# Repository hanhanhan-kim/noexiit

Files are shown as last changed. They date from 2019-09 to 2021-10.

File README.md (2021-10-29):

# NOEXIIT
> "*Hell is other [insects].*"
>
> \- Insects

NOEXIIT, or *NOvel Ethological X-Insect Interaction Task*, is a behaviour rig for presenting an ethological stimulus to an insect tethered on a floating ball. We originally developed NOEXIIT to present different kinds of pinned insects to a tethered walking beetle. 

This repository houses the software for controlling NOEXIIT. It is  a `pip`-installable Python package by the same name and is a CLI. It includes commands for calibrating and testing the rig, as well as commands for acquiring experimental data. I have tested the NOEXIIT CLI on Ubuntu 18.04. 

In addition to the CLI software, the repository features a `hardware/` directory, which contains all necessary custom design files, datasheets, a bill of materials, and assembly tips. 

## Installation:

1. Clone this repository:

   ```bash
   git clone https://github.com/hanhanhan-kim/noexiit
   ```

2. Install the Anaconda environment from the repo's root directory, where `conda_env.yaml` is housed:

   ```bash
   conda env create -f conda_env.yaml
   ```

   It will create an environment called `noexiit`.

3. Activate the environment:

   ```bash
   conda activate noexiit
   ```

4. Install the `noexiit` Python package from the repo's `software/` subdirectory:

   ```bash
   pip install -e .
   ```

## Dependencies:

In addition to the `noexiit` Python package installation, additional non-Python software and firmware must be installed. They are as follows:

### Spinnaker 

I use FLIR Blackfly S cameras (BFS-U3-04S2M-CS) and Spinnaker 1.27.0.48 for Ubuntu 18.04. This Spinnaker version is no longer available on the FLIR website and requires e-mailing FLIR customer support.  

### FicTrac

[My fork](https://github.com/hanhanhan-kim/fictrac_noexiit) of [Richard Moore's official `fictrac` repo](https://github.com/rjdmoore/fictrac) requires low-level software dependencies:

- `vcpkg` rolled back to commit `85211f3ab66e15c7669a1c14a25564afcf31e2e6`. 
- [cmake v.3.15.0](https://github.com/Kitware/CMake/releases/tag/v3.15.0).

### LabJack U3 DAQ

I use the LabJack U3-HV as my DAQ, which synchronizes my data streams in hardware.  Instructions for installing the `exodriver` library necessary for using the LabJack U3-HV are available [here](https://labjack.com/support/software/installers/exodriver).  I use LabJack's [Python module](https://github.com/labjack/LabJackPython) to interface with the LabJack U3-HV. Set up of the Anaconda environment already installs the LabJack Python module.

### Firmware

#### Multi-camera external trigger

[My fork](https://github.com/hanhanhan-kim/autostep) of [Will Dickson's official `camera_trigger` repo](https://github.com/willdickson/camera_trigger) requires firmware dependencies on an ATmega328P MCU. I use the following Arduino IDE dependencies:

- TimerOne v1.1.0
- Streaming v5.0.0
- ArduinoJson v5.13.5 (is _not_ compatible with v6.0.0+)
- Array v1.1.2 

Set up of the Anaconda environment already installs the software dependencies for [`camera_trigger`](https://github.com/hanhanhan-kim/autostep).

#### Stepper and servo motors

[My fork](https://github.com/hanhanhan-kim/autostep) of [Will Dickson's official `autostep` repo](https://github.com/willdickson/autostep) requires firmware dependencies on a Teensy 3.2 MCU. Uploading firmware onto a Teensy requires the [Teensyduino add-on for the Arduino IDE](https://www.pjrc.com/teensy/teensyduino.html). I use the following Arduino IDE dependencies:

- Streaming v5.0.0
- ArduinoJson v5.13.5 (is _not_ compatible with v6.0.0+)
- Array v1.1.2
- [SparkFun's L6470 AutoDriver library](https://github.com/sparkfun/L6470-AutoDriver/tree/master/Libraries/Arduino) (commit `734489ea1eaeb96cfab712c96817e35d9c942eb8`).

Set up of the Anaconda environment already installs the software dependencies for [`autostep`](https://github.com/hanhanhan-kim/autostep).

#### Valves

[My fork](https://github.com/hanhanhan-kim/switchx7) of [Will Dickson's official `switchx7` repo](https://github.com/willdickson/switchx7) requires firmware dependencies on a Teensy 3.2 MCU. Uploading firmware onto a Teensy requires the [Teensyduino add-on for the Arduino IDE](https://www.pjrc.com/teensy/teensyduino.html). I use the following Arduino IDE dependencies:

- Streaming v5.0.0

Set up of the Anaconda environment already installs the software dependencies for [`switchx7`](https://github.com/hanhanhan-kim/switchx7).

## How to use:

Using `noexiit` is simple! From anywhere, type the following in the command line:

```bash
noexiit
```

Doing so will bring up the menu of possible options and commands. To execute a command, specify the command of interest after `noexiit`. For example, to run the `print-config` command:

```bash
noexiit print-config
```

### The `.yaml` file

The successful execution of a command requires filling out a single `.yaml` configuration file. The configuration file provides the arguments for all of `noexiit`'s commands. By default, `noexiit` will look for a file calleld `config.yaml` in the directory from which you run a `noexiit` command. For this reason, I suggest that you name your `.yaml` file `config.yaml`. Otherwise, you can specify a particular `.yaml` file like so:

```bash
noexiit --config <path/to/config.yaml> <command>
```

For example, if the `.yaml` file you want to use has the path `~/tmp/my_weird_config.yaml`, and you want to run the `expt-pt-to-pt` command, you'd input:

```bash
noexiit --config ~/tmp/my_weird_config.yaml expt-pt-to-pt
```

Each key in the `.yaml` configuration file refers to a `noexiit` command. The value of each of these keys is a dictionary that specifies the parameters for that `vidtools` command. Make sure you do not have any trailing spaces in the `.yaml` file. An example `config.yaml` file is provided in the repository. 

### Commands

The outputs of `noexiit`'s commands never overwrite existing files, without first asking for user confirmation. `noexiit`'s commands and their respective `.yaml` file arguments are documented below:

#### `print-config`

<details><summary> Click for details. </summary>
<br>

This command prints the contents of the `.yaml` configuration file. It does not have any `.yaml` parameters.
</details>

#### `plot-pid-live`

<details><summary> Click for details. </summary>
<br>

This command plots and saves to a `.csv`, in real time, the voltage readings of the photo-ionization detector (PID). It assumes that the PID is connected to the **AIN 7** (low-voltage FIO) pin of the LabJack U3-HV . It uses a 'command and response' protocol, instead of a 'streaming' protocol. This command is useful for troubleshooting the PID, and is not recommended for experimental data acquisition. It does not have any `.yaml` parameters. 
</details>

#### `sniff-and-puff`

<details><summary> Click for details. </summary>
<br>

This command controls two two-way solenoid valve outputs, while also streaming the following 2 types of data to the LabJack U3 DAQ:
  1. Electrical copies of those output commands 
  2. PID data 
  
By default, the low-voltage pin, FIO7, is hard-coded as an analog input on the stream, and is meant to be hooked up to the PID signal. The high-voltage pin, AIN3, can be used instead, but the user must go into the codebase and alter the hard-coded value. The electrical copies of the valve control commands are sent via the D-sub connector to the [Teensy 3.2 breakout board](https://github.com/willdickson/teensy3x_solenoid_driver). This command assumes that the increasing numbering of the D-sub connector pins matches the increasing numbering of the breakout board pins, from the smallest possible pin values.  This command is useful for collecting troubleshooting data, but is probably not ideal for acquiring data for biological experiments.

This command's `.yaml` parameters are:

- `duration` (float or `null`): Duration (secs) of the DAQ stream. If `null`, will stream until exited (ctrl+c). 

- `output_dir` (string or `null`): The path to the directory where the acquired `sniffed_puffed.csv` data will be saved. If `null`, will inherit the value from the `calibrate` parameter in the `config.yaml` file. 

- `port` (string): The path to the Teensy MCU port that control the valves, e.g. `/dev/ttyACM1`. This path is *not* the Teensy MCU port that controls the stepper and servo motors. 

- `pre_stim_durn` (float): The time (secs) before activating only the 'ON' valve, e.g. the odour valve. 

- `stim_durn` (float): The time (secs) while activating only the 'ON' valve, e.g. the odour valve.

- `post_stim_durn` (float): The time (secs) after activating only the 'ON' valve, e.g. the odour valve. 

- `on_valve_id` (integer): The ID of the 'ON' valve. Will be a value between 0 and 6 inclusive. An appropriate valve for activating e.g. the odourant. 

- `off_valve_id` (integer): The ID of the 'OFF' valve. Will be a value between 0 and 6 inclusive. An appropriate valve for activating e.g. the solvent. 
</details>

#### `calibrate`

<details><summary> Click for details. </summary>
<br>

This command calibrates the linear servo's behaviour. It sets the servo's maximum extension angle to avoid crashes and overshoots, based on visual inspection. The servo can rotate around the rig's spherical treadmill, while being held at the set max extension angle. This function is useful for preparing closed-loop experiments. This command can also configure the acquired experimental data to a specific directory. Importantly, this command does not require the user to update the `config.yaml` file beforehand. Rather, the command updates the configuration file based on 'real-time' user inputs. Alternatively, this command does not need to be run, and the `config.yaml` file can be manually modified. This command's `.yaml` parameters are:

- `max_ext` (float): The max extension value of the linear servo(s). Must be a value between 0.0 and 180.0, inclusive. Running the `calibrate` command will automatically update this value.

- `output_dir` (string): The path to the directory where acquired data will be saved. Running the `calibrate` command can automatically update this value.
</details>

#### `expt-pt-to-pt`

<details><summary> Click for details. </summary>
<br>

This command moves the tethered stimulus to each angular position in a list of specified positions. Upon arriving at a position, the command extends the tethered stimulus for a fixed duration. Then retracts the tethered stimulus for a fixed duration. Streams data during motor movements. Events happen in the following order:

Initialization (homing, etc.)
│
├── Gets DAQ stuff
├── Gets motors' positions
├── Starts cam trigger
├── Starts valves, if necessary
├── Starts motors
│
├── Finishes motors or duration
├── Stops cam trigger
├── Stops getting motors' positions
├── Stops valves, if necessary
└── Stops getting DAQ stuff

Events happen in the above order even when the command is interrupted (ctrl + c).

"DAQ stuff" refers to the PID data and the frame counter. Motor position sets and gets happen in a different process from DAQ gets, in order to achieve maximum frequencies. 

This command's `.yaml` parameters are: 

- `duration` (float or `null`): Duration (secs) of the synchronized multi-cam video recordings. If set to `null`, will record until the motor sequence has finished. If using BIAS, the user MUST match this argument to the BIAS recordings' set duration. 

- `trigger_port` (string): The path to the ATMega328P MCU (e.g. Arduino Nano) that controls the valves, e.g. `/dev/ttyUSB0`. 

- `cam_hz` (integer): The frame rate, in Hz, with which to fire the external camera trigger. 

- `poke_speed` (integer): A scalar speed factor for the tethered stimulus' extension and retraction. Must be positive. 10 is the fastest. Higher values are slower. 

- `ext_wait_time` (float): Duration (secs) for which the tethered stimulus is extended at each set angular position. 

- `retr_wait_time` (float): Duration (secs) for which the tethered stimulus is retracted at each set angular position. 

- `positions` (list of floats): List of angular positions (degs) for the tethered stimulus to visit. The tethered stimulus will extend and retract at each position in the list. E.g. `[0, 180.3, -180, 720]` will result in the stepper motor rotating clockwise to all the positive values and rotating counter clockwise to all the negative values. 

- `extension` (float or `null`): The maximum linear servo extension angle. If `null`, will inherit the value from the `calibrate` parameter in the `config.yaml` file. 

- `puff_port` (string or `null`): The path to the Teensy MCU that controls the valves, e.g. `/dev/ttyACM1`. This path is *not* the Teensy MCU port that controls the stepper and servo motors. Importantly, **if this argument is `null`, none of the valve arguments will be considered** (i.e. any arguments with the words `puff` or `valve`). 

- `pre_puff_durn` (float): The time (secs) before activating only the 'ON valve, e.g. the odour valve. This argument is a 'valve argument'. 

- `puff_durn` (float): The time (secs) while activating only the 'ON' valve, e.g. the odour valve. This argument is a 'valve argument'. 

- `post_puff_durn` (float): The time (secs) after activating only the 'ON' valve, e.g. the odour valve. This argument is a 'valve argument'. 

- `on_valve_id` (integer): The ID of the 'ON' valve. Will be a value between 0 and 6 inclusive. An appropriate valve for activating e.g. the odourant. This argument is a 'valve argument'. 

- `off_valve_id` (integer): The ID of the 'OFF' valve. Will be a value between 0 and 6 inclusive. An appropriate valve for activating e.g. the solvent. This argument is a 'valve argument'. 

**N.B.** Successful execution of this command requires some external set-up. The BIAS video capture program must be manually launched before running the command. In addition, even though the command can automatically configure and initiate BIAS for synchronized multi-cam acquisition via HTTP commands, the HTTP commands are unreliable and work only sometimes. For this reason, I recommend manually uploading the same BIAS configuration file for each camera, such that the external trigger feature is enabled, and then manually initiating the external trigger listening by clicking on each camera GUI's `Start` button (in external trigger mode, the `Start` button doesn't actually start acquisition. It just initiates the 'listening' for an external trigger signal).
</details>

#### `expt-still-robot`

<details><summary> Click for details. </summary>
<br>

This command moves the tethered stimulus at 1) an angular velocity opposite in direction, and adjustable in magnitude, to the animal on the ball (stepper motor), and 2) to some distance away or towards the animal on the ball, given the tethered  stimulus' angular position (linear servo). The idea is to mimic a stationary  stimulus in a flat planar world. The animal turning right and away from a stimulus in front of it, in the planar world, is equivalent to the stimulus turning left and retracting away from the animal, in the on-a-ball world. This command demonstrates the closed-loop capabilities of NOEXIIT. The data is saved as a `.csv` file in the `output_dir` specified by `config.yaml`'s `calibrate` parameter. 

It assumes an ATMega328P-based camera trigger, even if as of 2021/10/25, this command operates only a single camera. 

This command's `.yaml` parameters are:

- `duration` (float): Duration (secs) of the closed-loop acquisition mode. 

- `k_stepper` (float): Gain term for modifying the significance of the animal's turns. A value of 1 means that when the animal turns theta degrees, the stimulus also rotates theta degrees, but in the opposite direction. A value less than 1 means that when the animal rotates theta degrees, the stimulus rotates less than theta degrees by a factor of `k_stepper`, and in the opposite direction. In this way, the animal's actions are 'less significant' than they normally are. A value greater than 1 means that when the animal rotates theta degrees, the stimulus rotates more than theta degrees by a factor of `k_stepper`, and in the opposite direction. In this way, the animal's actions are 'more significant' than they normally are. 

- `ball_radius` (float): Radius of the spherical treadmill, in mm. 

- `fictrac_exe_path` (string): Path to the Fictrac executable. Will probably be the absolute path of `fictrac/bin/fictrac`, where the parent directory is the Fictrac repo. 

- `fictrac_config_path` (string): Path to the Fictrac configuration text file. *N.B.* The configuration file must have an integer as the `src_fn` parameter, as opposed to a path that specifies an offline video. 
</details>

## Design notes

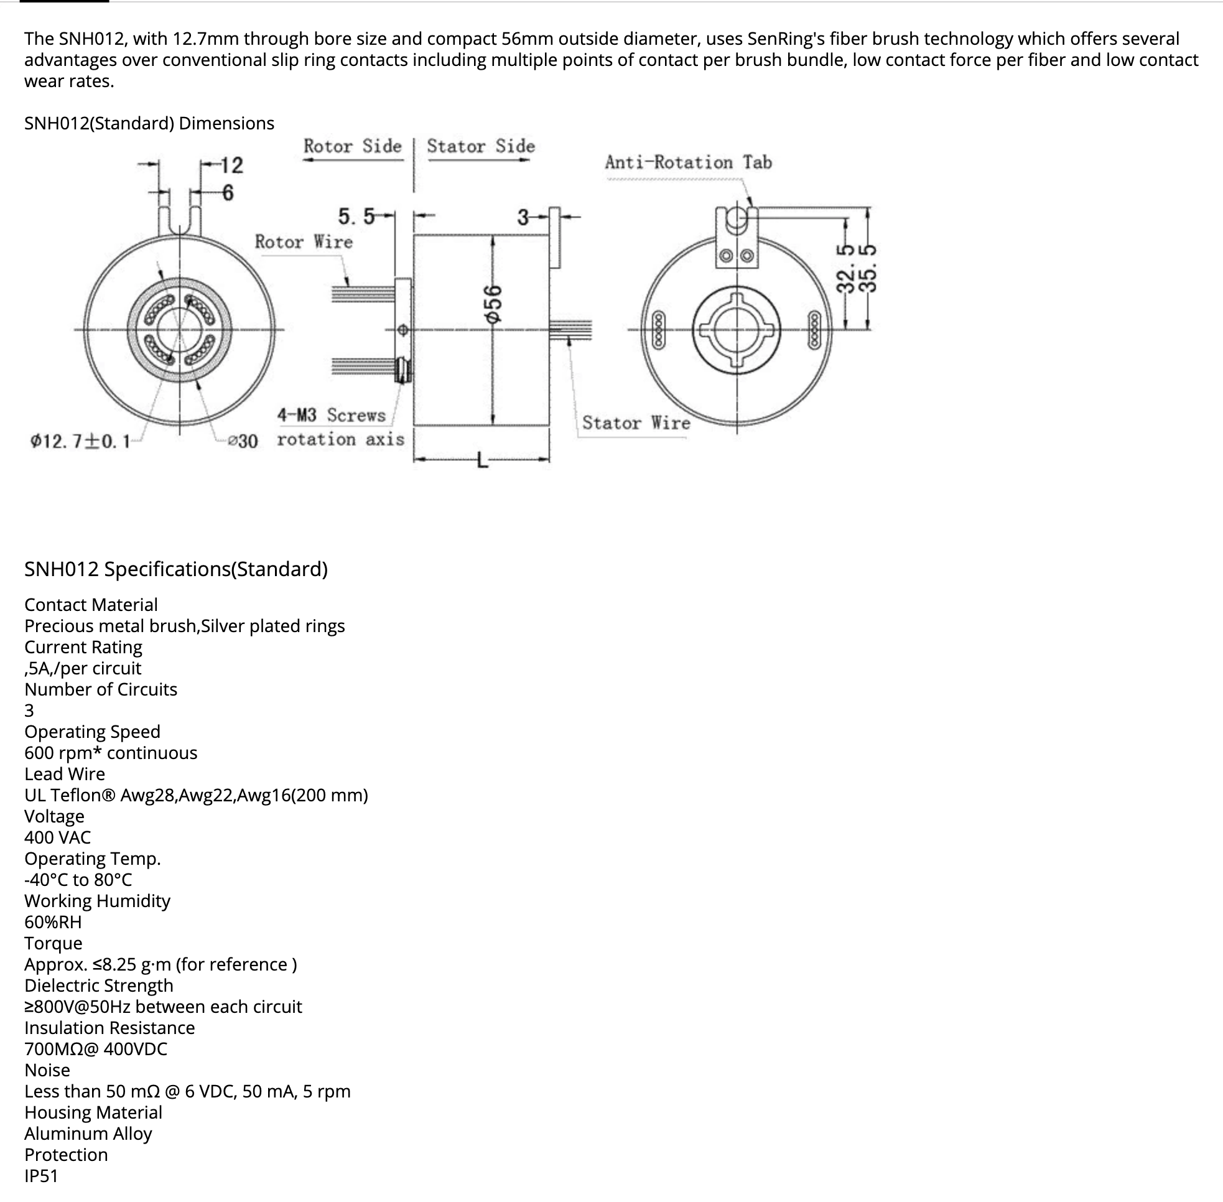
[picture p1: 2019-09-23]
hardware/datasheets/senring_snh012.png

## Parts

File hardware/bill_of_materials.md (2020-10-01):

# BOM

## Commercial Parts: Stimulus Presentation

In addition to the parts in the below table, I recommend:

- 1/4"-20 x 3/8" and x 1" screws, and 1/4"-20 washers
- 8-32 x 1/4", x 3/8", and x 1/2" screws, and 8-32 washers
- 6-32 x 1/4", x 3/8", and x 1/2" screws 
- M2.5 x 12 mm ([McMaster-Carr 91292A016](https://www.mcmaster.com/91292A016/)) screws
- 6-32 x 3/8" ([McMaster-Carr 92220A142](92220A142)) and x 1/2" ([McMaster-Carr 92220A183](https://www.mcmaster.com/92220A183/)) specialty low-profile socket-head screws

For most cases in this build, the 3/8" length and 1/2" length screws of a given threading are interchangeable, but best practice it to use the shortest length screws whenever possible. Remember to apply all screws evenly. 

| Vendor        | Product no.                                                  | Price per unit (USD) | Quantity | Description                                                  |
| ------------- | ------------------------------------------------------------ | -------------------- | -------- | ------------------------------------------------------------ |
| Thor Labs     | [MB12](https://www.thorlabs.com/thorproduct.cfm?partnumber=MB12) | 155.53               | 1        | Aluminum breadboard, 12"x12"x1/2", 1/4"-20 taps              |
| Servocity     | [615420](https://www.servocity.com/5mm-15-tooth-pinion-pulley/) | 8.99                 | 1        | 15 tooth pinion pulley. .40” inside the flanges allow for belts up to 3/8” in width. |
| Sparkfun      | [ROB-13656](ROB-13656)                                       | 30.95                | 1        | NEMA 23 stepper motor, 200 steps per revolution (1.8 degree step angle), 3.2 V, 2.0 A/phase, 2-phase, recommended holding torque of 125 oz.in. An equivalent part can be used, provided it is 200 steps per revolution. |
| McMaster-Carr | [93505A683](https://www.mcmaster.com/93505A683/)             | 9.32                 | 2        | Aluminum male-female threaded hex standoff. 1/2" hex size, 3 1/2" long, 1/4"-20 thread size. |
| McMaster-Carr | [93505A459](https://www.mcmaster.com/93505A459/)             | 1.12                 | 4        | Aluminum male-female threaded hex standoff. 1/4" hex size, 2" long, 8-32 thread size. |
| Servocity     | [B375-110XL](https://www.servocity.com/11-55t-3-8-wide-xl-timing-belt/) | 4.05                 | 1        | XL series timing belt, 3/8” wide, 1/5 pitch (5.08mm) . Neoprene with fiberglass cords. 11" circumference, 55 teeth. |
| McMaster-Carr | [92510A765](https://www.mcmaster.com/92510A765/)             | 1.65                 | 4        | Aluminum unthreaded spacer, 1/2" OD, 1/2" length for 1/4" screw size. |
| Servocity     | [545588](https://www.servocity.com/0-250-0-770-clamping-hub/) | 6.99                 | 1        | 1/4" aluminum clamping hub.                                  |
| McMaster-Carr | [89895K722](https://www.mcmaster.com/89895K722/)             | 11.26                | 1        | Smooth-bore seamless 304 stainless steel tubing, 1/4" OD, 0.02" wall thickness, 1 ft length. Cut to length. |
| SDP/SI        | [A 6C 3-15DF03716](https://shop.sdp-si.com/catalog/product/?id=A_6C_3-15DF03716) | 13.30                | 1        | 0.200" (XL) pitch, 15 teeth, 0.5" bore, 2 flanges with hub, carbon steel timing pulley for 0.375" wide belt. |
| Siskiyou      | [09380000E](https://www.siskiyou.com/rtc-0-5-09380000e.html) | 22.00                | 1        | Rotation and translation rod clamp for securing 1/2" OD posts and shafts. |
| Servocity     | [634230](https://www.servocity.com/0-500-1-2-x-4-00-stainless-steel-precision-shafting/) | 3.59                 | 1        | 1/2" bore, stainless steel shaft, 4" length stock.           |
| Servocity     | [545600](https://www.servocity.com/0-500-0-770-clamping-hub/) | 5.99                 | 3        | 1/2" aluminum clamping hub.                                  |
| Servocity     | [585424](https://www.servocity.com/90-single-angle-pattern-bracket/) | 1.89                 | 1        | 90 degree aluminum single angle pattern bracket              |
| Servocity     | [585506](https://www.servocity.com/90-single-angle-short-pattern-bracket/) | 1.99                 | 1        | 90 degree aluminum single angle short pattern bracket        |
| Servocity     | [535138](https://www.servocity.com/1-2-bore-side-tapped-pillow-block/) | 8.49                 | 2        | 1/2" bore, side-tapped pillow block                          |
| Senring       | [SNH012-0305](https://www.aliexpress.com/item/1435888748.html?spm=2114.12010612.8148356.39.10d02ac30XPlud) | 75.00                | 1        | Senring SNH012 slip ring, 12.7 mm hole size, 3 circuits each 5 A, outer diameter 56 mm. |
| Servocity     | [635262](https://www.servocity.com/0-500-1-2-x-12-00-aluminum-tubing/) | 4.59                 | 1        | 1/2" aluminum tube, 12" length stock, .030" wall thickness. Cut to length. |
| Servocity     | [535118](https://www.servocity.com/1-2-bore-face-thru-hole-pillow-block/) | 7.99                 | 1        | 1/2" bore, face thru-hole pillow block                       |
| McMaster-Carr | [96905K39](https://www.mcmaster.com/96905K39/)               | 5.83                 | 4        | Vibration-damping sandwich mount with stud and insert, 6-32 thread |
| Servocity     | [545548](https://www.servocity.com/0-250-0-770-set-screw-hub/) | 5.99                 | 1        | 1/4" diameter, aluminum pattern set screw hub.               |
| Servocity     | [545360](https://www.servocity.com/side-tapped-pattern-mount-c/) | 5.99                 | 1        | Side-tapped pattern mount C.                                 |
| Servocity     | [545556](https://www.servocity.com/0-375-0-770-set-screw-hub/) | 4.99                 | 2        | 3/8" diameter, aluminum pattern set screw hub.               |
| Servocity     | [635250](https://www.servocity.com/0-375-3-8-x-12-00-aluminum-tubing/) | 4.09                 | 1        | 3/8" aluminum tube, 12" length stock, .035" wall thickness. Cut to length. |
| IR Robot USA  | [L12-40PT-3](https://www.irrobotusa.com/products/premium-mighty-zap-mini-linear-servo-12v?_pos=1&_sid=07ad8e762&_ss=r) | 114.00               | 1        | Mini linear actuator, 12 V, 12 N, 110.0 mm/s, PWM protocol, 27 mm stroke length |
| Digi-Key      | [HE667-ND](https://www.digikey.com/product-detail/en/littelfuse-inc/MITI-3V1-6-8/HE667-ND/859130) | 2.14                 | 1        | Reed switch for homing.                                      |
|               |                                                              |                      |          | Magnet for triggering the reed switch.                       |

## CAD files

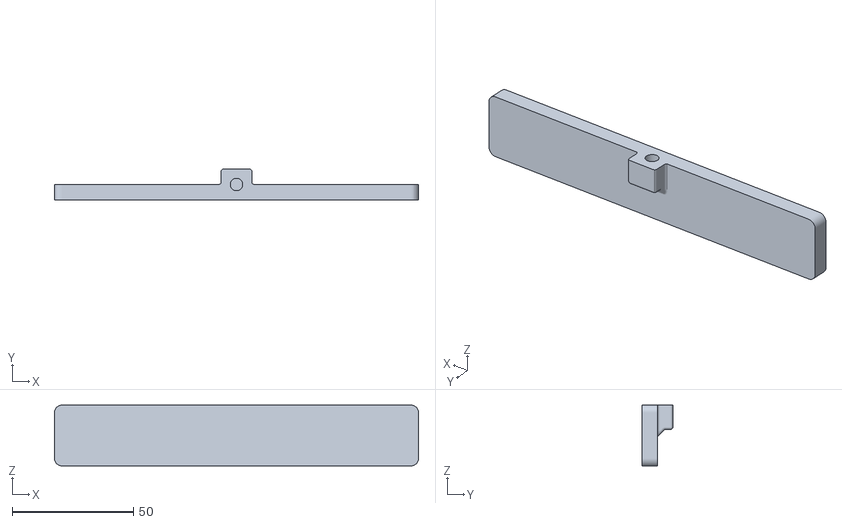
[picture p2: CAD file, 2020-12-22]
hardware/customs_3Dprint/backlight_on_rail_carrier.stl
150.0 x 12.7 x 25.0

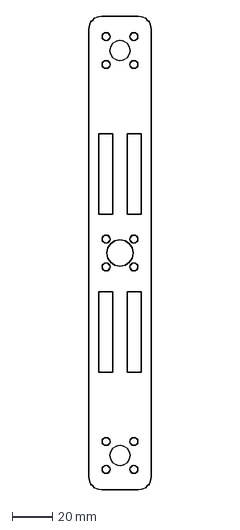
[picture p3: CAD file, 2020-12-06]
hardware/customs_lasercut/support_layer1_doubled_platyusa_compatible.dxf
31.0 x 235.0 mm

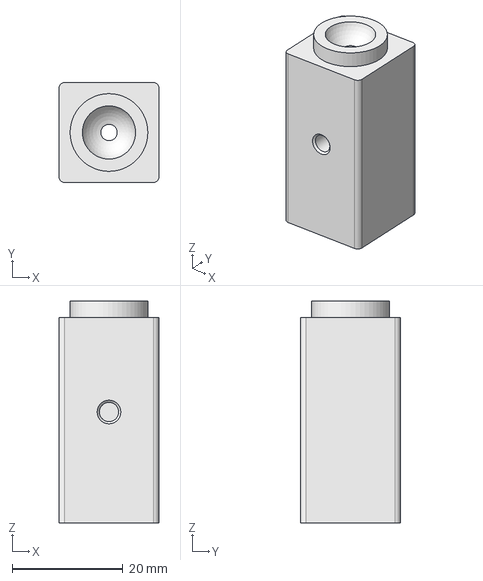
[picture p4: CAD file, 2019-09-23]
hardware/customs_machining/ball_fixture_10mm_dia_wbd/floating_ball_fixture_10mm.step
18.0 x 18.0 x 40.0 mm

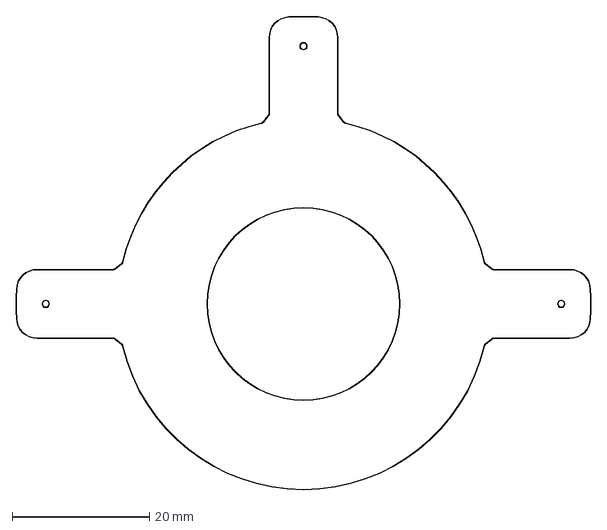
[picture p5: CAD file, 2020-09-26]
hardware/customs_machining/ring_light_to_cam_clamping_mount/clamping_mount_for_waterjet.dxf
83.6 x 68.8 mm

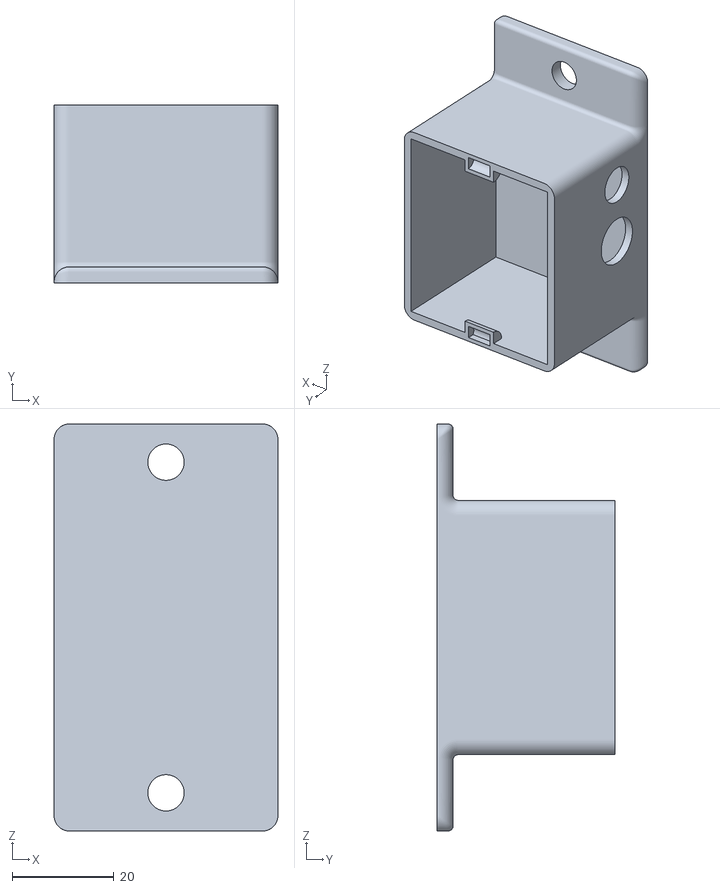
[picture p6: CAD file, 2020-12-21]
hardware/customs_3Dprint/light_switch_box.stl
44.0 x 35.0 x 80.0

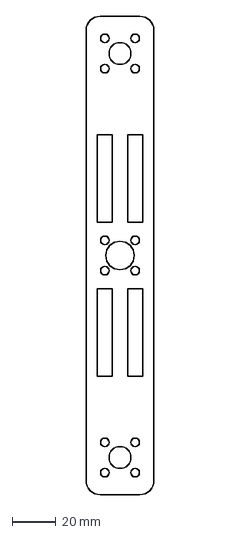
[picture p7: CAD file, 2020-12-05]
hardware/customs_lasercut/support_layer1_doubled.dxf
31.0 x 219.0 mm

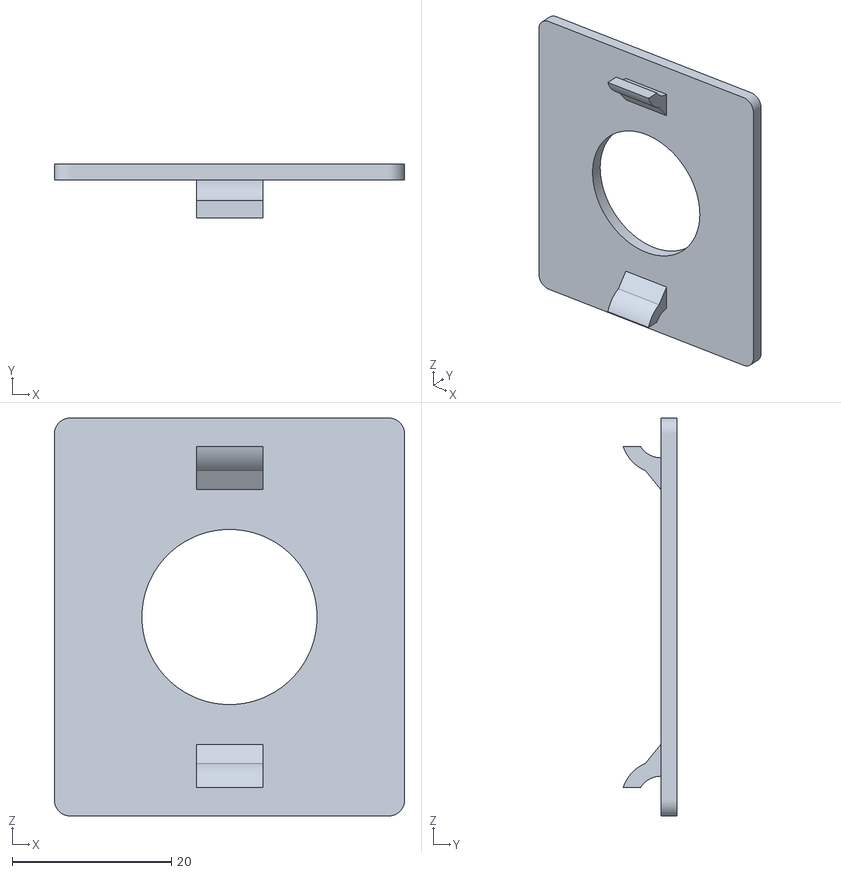
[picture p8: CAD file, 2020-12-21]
hardware/customs_3Dprint/light_switch_lid.stl
44.0 x 6.74 x 50.0

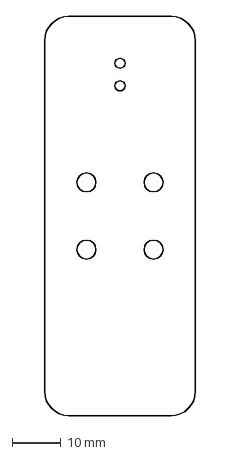
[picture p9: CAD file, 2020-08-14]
hardware/customs_lasercut/support_layer2.dxf
31.0 x 82.0 mm

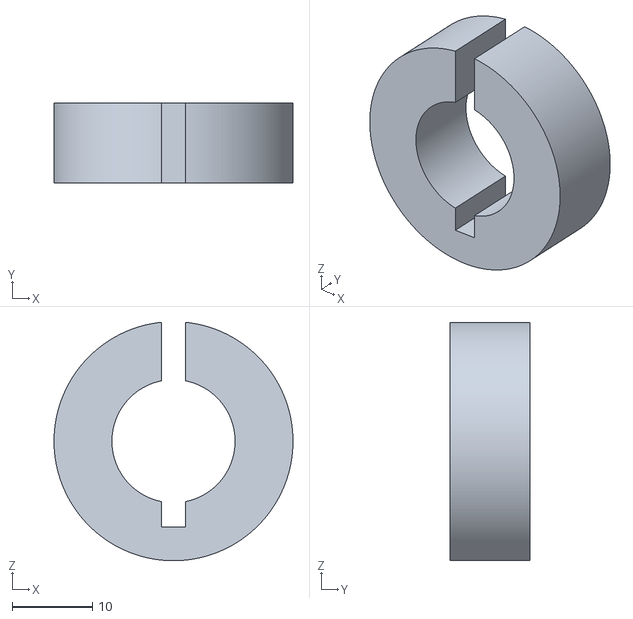
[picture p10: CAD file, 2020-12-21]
hardware/customs_3Dprint/clamping_mount_InfiniGage_to_InfiniStix_adaptor.stl
29.7 x 10.0 x 29.6

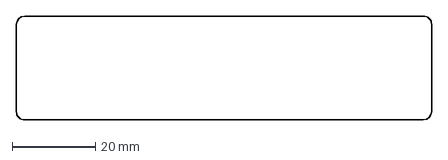
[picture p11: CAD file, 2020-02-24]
hardware/customs_lasercut/front_cam_backlight_platform.dxf
100.0 x 25.0 mm

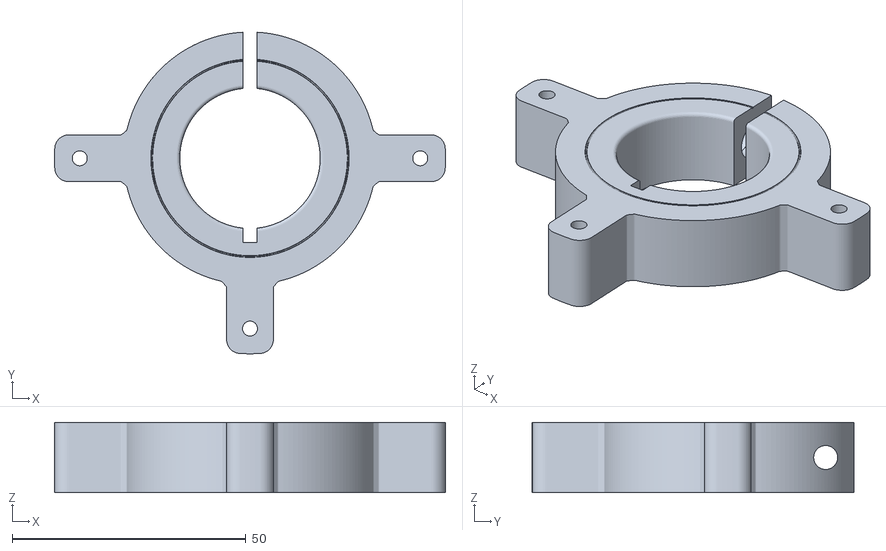
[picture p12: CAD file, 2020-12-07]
hardware/customs_3Dprint/clamping_mount_with_brass_inserts_Uxcell_72_IR_LED_ring_to_InfiniGage.stl
83.6 x 68.8 x 15.0

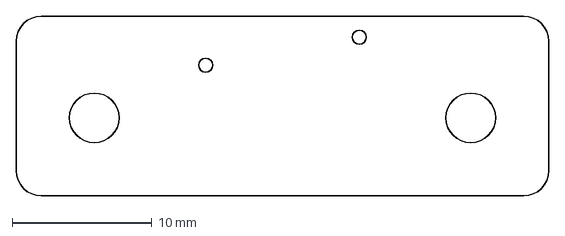
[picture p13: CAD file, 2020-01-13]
hardware/customs_lasercut/reedswitch_fixture_on_servocity_585506.dxf
38.1 x 12.9 mm

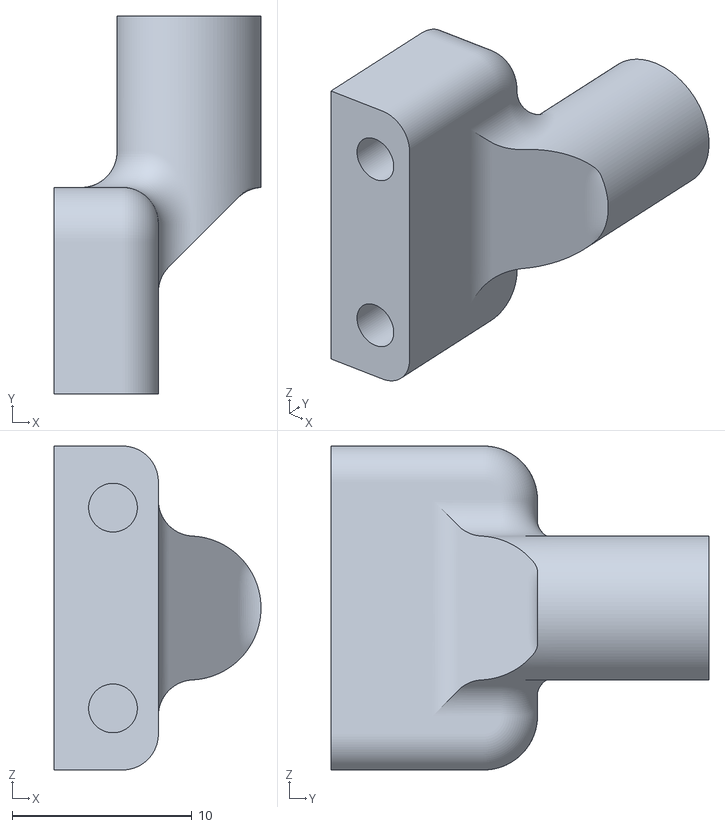
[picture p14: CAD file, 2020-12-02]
hardware/customs_3Dprint/slipring_opposite_immobilizer.stl
11.5 x 21.0 x 18.0

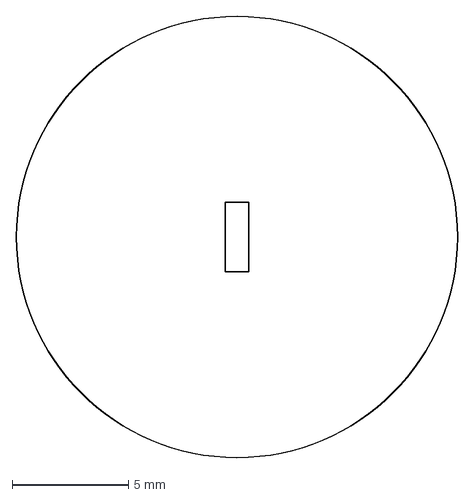
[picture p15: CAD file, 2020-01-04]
hardware/customs_lasercut/magnet_fixture.dxf
19.0 x 19.0 mm

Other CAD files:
hardware/customs_3Dprint/slipring_immobilizer.stl
hardware/customs_lasercut/support_layer4.dxf
hardware/customs_3Dprint/jig_for_milling_countersink_for_ring_light.stl
hardware/customs_lasercut/nema23_57BYGH420-2_to_14-20_breadboard_adaptor_layer1.dxf
hardware/customs_3Dprint/connector_ball_fixture_to_3-8_tube.stl
hardware/customs_lasercut/EM3242_breakoutboard_mount.dxf
hardware/customs_lasercut/nema23_57BYGH420-2_to_14-20_breadboard_adaptor_layer2.dxf
hardware/customs_lasercut/servocity_SKU545556_to_14-20_breadboard_adaptor_multiY.dxf
hardware/customs_lasercut/spacer_servocity_585506.dxf
hardware/customs_lasercut/spacer_servocity_SKU585424.dxf
hardware/customs_lasercut/support_layer1.dxf
hardware/customs_lasercut/support_layer3.dxf
hardware/customs_machining/ball_fixture_10mm_dia_wbd/floating_ball_fixture_10mm.fcstd
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

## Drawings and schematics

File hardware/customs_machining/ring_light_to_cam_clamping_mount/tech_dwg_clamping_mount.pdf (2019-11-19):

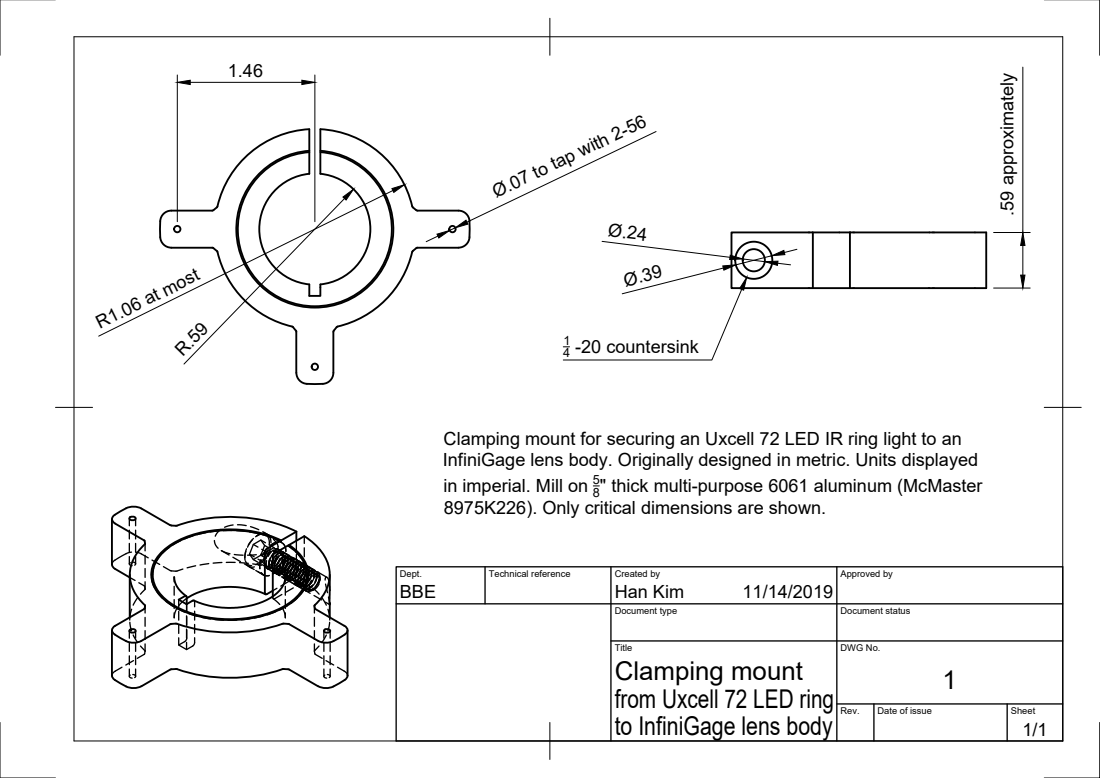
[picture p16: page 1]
R.59 R1.06 at most; 1/4-20 countersink; .59 approximately

Ø.07 to tap with 2-56

Clamping mount for securing an Uxcell 72 LED IR ring light to an
InfiniGage lens body. Originally designed in metric. Units displayed
in imperial. Mill on 5
8975K226). Only critical dimensions are shown.

" thick multi-purpose 6061 aluminum (McMaster

Dept. BBE | Technical reference | Created by Han Kim 11/14/2019 | Approved by

Document type | Document status

Title Clamping mount from Uxcell 72 LED ring to InfiniGage lens body | DWG No. 1

Rev. | Date of issue | Sheet 1/1

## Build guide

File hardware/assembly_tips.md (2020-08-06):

## Alternate Parts

| Vendor      | Product no. | Price per unit (USD) | Quantity     | Description                                                 |
| ----------- | ----------- | -------------------- | ------------ | ----------------------------------------------------------- |
| Cole-Parmer | EW-45501-66 | 27.60                | 1 pack of 25 | Female-luer x 1/4-28 UNF thread. Polycarbonate.             |
| Cole-Parmer | SI-45518-00 | 13.30                | 1 pack of 25 | Male-luer with lock ring x 1/16" hose  barb. Polypropylene. |
|             |             |                      |              |                                                             |

Driver pinion: 15 teeth; Driven pulley wheel: 36 teeth; speed ratio = 36/15 = 2.4 x

- Talk about alternative parts
  - Stepper motor; see phidget
  - Timing belt; SDP/SI: A 6B 3-040037 alternative; most lengths of at least __ should work so long as it's XL pitch, just adjust accordingly
  - Pinions; will determine resulting gear ratio
- Talk about creating sufficient tension by pulling on the slotted fixtures before anchoring to breadboard
- VERY IMPORTANT: In order to reduce vibrations, make sure the belt isn't over-tensioned. Too much tension pulls on the rotary tube, which causes it to be not directly straight and perpendicular to the breadboard. The tube's rotation then becomes a little diagonaled, which transmits the vibrations. Similarly, it's important to adjust all the parts that are secured onto the breadboard. A helpful tip is to run the air to the ball and make sure that the ball exhibits 'ambient' rotations. If the ball is quickly moving in a single direction, adjust the positioning and securing of the parts to the breadboard, until ambient rotations of the ball are observed.
- Remember to talk about adjusting the firmware on the L12-40PT-3 linear servo.

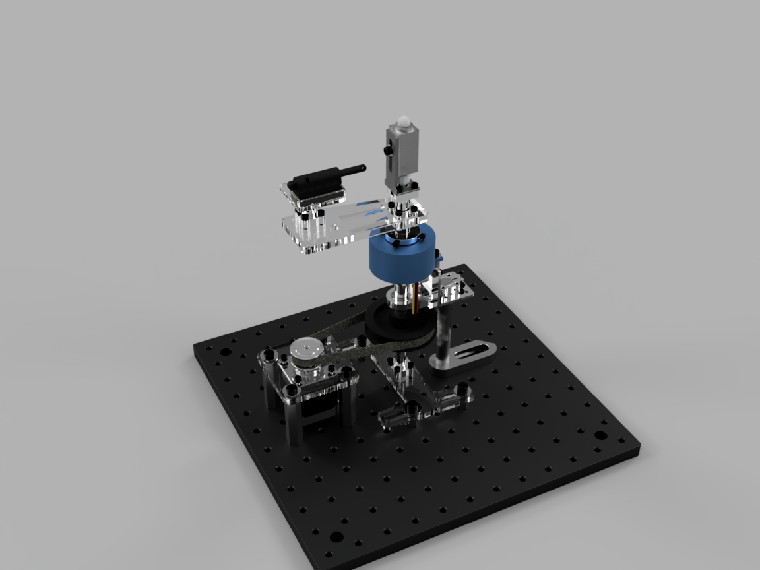
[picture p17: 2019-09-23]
hardware/renders/assembly_high_res.png

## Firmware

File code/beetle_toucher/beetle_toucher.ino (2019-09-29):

// Set the current limit to 2400 mA.
// Documentation: http://pololu.github.io/high-power-stepper-driver

// SET-UP -----------------------------------------------------------------------

#include <Servo.h>
#include <SPI.h>
#include <HighPowerStepperDriver.h>

// Servo pin:
const uint8_t servo_pin = 9;
// Stepper pins:
const uint8_t dir_pin = 2;
const uint8_t step_pin = 3;
const uint8_t cs_pin = 4;

// Initialize my servo as a servo:
Servo servo;
// Initialize my stepper as a high-powered stepper:
HighPowerStepperDriver sd;

// Initialize my servo pos as position 0;
int pos = 0;

// This period is the length of the delay between steps, which controls the
// stepper motor's speed.  You can increase the delay to make the stepper motor
// go slower.  If you decrease the delay, the stepper motor will go faster, but
// there is a limit to how fast it can go before it starts missing steps.
const uint16_t StepPeriodUs = 100;
// Define the microstepping size (not the reciprocal, e.g. not 1/32, but 32)
int microstepping = 32;

// FUNCTIONS -----------------------------------------------------------------------

float read_float() {
  union u_tag {
    byte b[4];
    float floatval;
  } u;
  u.b[0] = Serial.read();
  u.b[1] = Serial.read();
  u.b[2] = Serial.read();
  u.b[3] = Serial.read();
  return u.floatval;
}

// Sends a pulse on the STEP pin to tell the driver to take one step, and also
//delays to control the speed of the motor.
void step()
{
  // The STEP minimum high pulse width is 1.9 microseconds.
  digitalWrite(step_pin, HIGH);
  delayMicroseconds(3);
  digitalWrite(step_pin, LOW);
  delayMicroseconds(3);
}

// Writes a high or low value to the direction pin to specify what direction to
// turn the motor.
void setDirection(bool dir) {
  // The STEP pin must not change for at least 200 nanoseconds before and after
  // changing the DIR pin.
  delayMicroseconds(1);
  digitalWrite(dir_pin, dir);
  delayMicroseconds(1); 
}

void rotate(float deg_increm) {
  setDirection(deg_increm > 0);

  // fullstep is 0.9 deg, gear ratio is 2.4
  unsigned int step_increm = round(2.4 * abs(deg_increm) / 0.9 * microstepping);
  //unsigned int step_increm = 400 * microstepping;
  for (unsigned int i = 0; i <= step_increm; i++) {
    step();
    delayMicroseconds(StepPeriodUs); 
  }
}

int servo_pos = 0;
void init_servo() {
  /*
  servo.write(servo_pos);
  delay(2700);
  */
  for (int pos = 180; pos > 0; pos--) {
    servo.write(pos);
    delay(15);
  }
}


void lineate(float mm_increm) {
  int target_servo_pos = round(mm_increm * 9);
  
  int servo_step;
  if (target_servo_pos >= servo_pos) {
    servo_step = 1;
  } else {
    servo_step = -1;
  }
  
  for (int pos = servo_pos; pos != target_servo_pos; pos += servo_step) {
    servo.write(pos);
    delay(15);
  }
  servo.write(target_servo_pos);
  delay(15);
  servo_pos = target_servo_pos;
}

// RUN ONCE ------------------------------------------------------------------------
void setup()
{
  // Attach the servo to the servo pin.
  servo.attach(servo_pin);

  SPI.begin();
  sd.setChipSelectPin(cs_pin);

  // Initialize the STEP and DIR pins to low.
  pinMode(step_pin, OUTPUT);
  digitalWrite(step_pin, LOW);
  pinMode(dir_pin, OUTPUT);
  digitalWrite(dir_pin, LOW);

  // Give the driver 1 ms to power up.
  delay(1);

  // Reset the driver to its default settings and clear latched status conditions.
  sd.resetSettings();
  sd.clearStatus();

  // Select auto mixed decay. TI's DRV8711 documentation recommends the auto mixed decay mode.
  sd.setDecayMode(HPSDDecayMode::AutoMixed);

  // Set the current limit.
  sd.setCurrentMilliamps36v4(2400);

  // Set the number of microsteps that corresponds to one full step.
  // sd.setStepMode(HPSDStepMode::MicroStep32);
  if (microstepping == 1) {
    sd.setStepMode(HPSDStepMode::MicroStep1);
  } else if (microstepping == 2) {
    sd.setStepMode(HPSDStepMode::MicroStep2);
  } else if (microstepping == 4) {
    sd.setStepMode(HPSDStepMode::MicroStep4);
  } else if (microstepping == 8) {
    sd.setStepMode(HPSDStepMode::MicroStep8);
  } else if (microstepping == 16) {
    sd.setStepMode(HPSDStepMode::MicroStep16);
  } else if (microstepping == 32) {
    sd.setStepMode(HPSDStepMode::MicroStep32);
  } else if (microstepping == 64) {
    sd.setStepMode(HPSDStepMode::MicroStep64);
  } else if (microstepping == 128) {
    sd.setStepMode(HPSDStepMode::MicroStep128);
  } else if (microstepping == 256) {
    sd.setStepMode(HPSDStepMode::MicroStep256);
  }
  
  // Enable the motor outputs.
  sd.enableDriver();

  Serial.begin(9600);

  init_servo();
}

// RUN INFINITELY -------------------------------------------------------------------
void loop()
{ /*
  rotate(360);
  delay(1000);
  rotate(-360);
  delay(1000);*/
  /*
  servo.write(40);
  delay(15);
  servo.write(60);
  delay(15);
  */

  /*
  lineate(5.5);
  delay(1000);
  lineate(15.5);
  delay(1000);
  */
  
  /*
  for (int pos = 0; pos < 180; pos++) {
    servo.write(pos);
    delay(15);
  }
  for (int pos = 180; pos > 0; pos--) {
    servo.write(pos);
    delay(15);
  }
  */
  float curr_mm_increm = read_float();
  float curr_deg_increm = read_float();
  lineate(curr_mm_increm);
  rotate(curr_deg_increm);
}

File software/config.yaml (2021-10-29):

calibrate:
  max_ext: 180.0
  output_dir: /mnt/more_vids/

sniff-and-puff:

  duration: null
  output_dir: null

  port: /dev/ttyACM1
  pre_stim_durn: 2
  stim_durn: 2
  post_stim_durn: 2
  on_valve_id: 1
  off_valve_id: 0
  
expt-pt-to-pt:
  trigger_port: /dev/ttyUSB0
  cam_hz: 100
  duration: 20 # secs
  # Motor stuff:
  ext_wait_time: 2 # secs
  extension: 90
  poke_speed: 10
  positions:
  - 180
  - 0
  retr_wait_time: 2
  # Valve stuff:
  puff_port: /dev/ttyACM1 # if null, none of the valve params will be considered
  pre_puff_durn: 2
  puff_durn: 2
  post_puff_durn: 2
  on_valve_id: 1
  off_valve_id: 0

expt-still-robot:
  duration: 30 # secs
  k_stepper: 1
  ball_radius: 5 # mm
  fictrac_exe_path: ~/src/fictrac_noexiit/bin/fictrac
  fictrac_config_path: ~/src/fictrac_noexiit/my_scripts/config_c_loop.txt  

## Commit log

2019-09-23 Initial commit. Bulk of hardware set-up complete. Not much code yet.
    [clamping_mount_Uxcell_72_IR_LED_ring_to_InfiniGage.stl, connector_ball_fixture_to_3-8_tube.stl, floating_ball_fixture_10mm.fcstd, floating_ball_fixture_10mm.st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]
2019-09-23 Basic code that operates the stepper motor and the linear actuator, but not in parallel.
2019-09-23 Renders of assembly and their motions
2019-09-25 Used conditionals to enable parallel movements of motors
2019-09-29 Cleaned up code, sequential execution of stepper and servo.
2019-09-29 Added support for Python to Arduino interface
2019-10-14 Started adding closed-loop control between FicTrac and motors.
2019-11-04 started changing code to work with Teensy and Sparkfun L6470 instead of Arduino and Pololu 36v4
2019-11-19 added design files for manufacturing an aluminum version of the ring light clamping mount
    [jig_for_milling_countersink_for_ring_light.stl, undersized_clamping_mount_Uxcell_72_IR_LED_ring_to_InfiniGage.DXF]
2019-11-19 added a mount for attaching an EM3242 angle sensor above the stepper motor
    [EM3242_breakoutboard_mount.dxf]
2019-11-19 a spacer for ensuring proper concentric alignment between stator and rotor bearing
    [spacer_servocity_585506.dxf]
2019-12-11 added assembly tips to reduce vibrations
2019-12-11 added parts for supporting the EM3242 angle sensor
2019-12-11 platform for supporting the EM3242 angle sensor
    [EM3242_breakoutboard_mount.dxf]
2020-01-04 Added initial Python scripts for controlling rig
    [output.csv]
2020-01-04 Replaced laser cut parts of NEMA17 and Actuonix servo for NEMA23 and MightyZap servo, respectively
    [magnet_fixture.dxf, nema17_42BYGHM810_to_14-20_breadboard_adaptor.dxf, nema23_57BYGH420-2_to_14-20_breadboard_adaptor_layer1.dxf, nema23_57BYGH420-2_to_14-20_b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]
2020-01-04 Added datasheets for MightyZap servo and NEMA23 stepper
2020-01-04 Added undersized plans for waterjetting the ring light clamps for cams
    [undersized_clamping_mount_Uxcell_72_IR_LED_ring_to_InfiniGage.DXF]
2020-01-04 Deleted code that was only compatible with old Pololu 36v4 driver and Arduino MCU
    [stepper_42BYGHM810_to_14-20_breadboard_adaptor.dxf]
2020-01-05 Added camera trigger commands
2020-01-05 Initialized script for setting and getting servo and stepper simultaneously
2020-01-05 Fixed stepper position csv output to the positions saved from list
2020-01-06 Fixed missing argument for stepper thread
2020-01-09 Tested stepper and servo commands without cam. Fixed percent str format error.
2020-01-10 Deleted csv file--csvs should be in gitignore
    [output.csv]
2020-01-10 Changed servo commands to blocking
2020-01-13 Added laser cutter files for the reed switch fixture
    [reedswitch_fixture_on_servocity_585506.dxf]
2020-01-16 Added a calibration script that adjusts the max extension of the linear servo according to user
2020-01-17 Replaced old stepper motor datasheet with current one
2020-01-17 Wrote servo calibration variable to a file
2020-01-17 Added in reading of servo calibration value
2020-01-22 Added manual for adjusting Mighty Zap linear servo firmware
2020-01-23 Added saving of motor parameters to files
2020-01-23 Changed formatting of motor parameter save to file output
2020-01-28 Renamed calibrate.py
2020-02-02 Specified the use of Python 2 when using camera_trigger, for now
2020-02-03 Placed camera trigger inside its own thread
2020-02-04 Fixed check for get current json and compare with target json
2020-02-04 Added continue? prompt before frame capture and printed status statements
2020-02-06 Uncommented trigger thread joining--forgot to uncomment
2020-02-24 Added front cam backlight platform
    [front_cam_backlight_platform.dxf]
2020-03-07 Adapt closed loop for autostep motors and FicTrac input
2020-03-11 Init real-time butter filter, courtsey of Will Dickson
2020-03-11 Fixed numpy error when applying real-time Butter filter
2020-03-11 Fix filtering--put filter outside of loop ... you idiot.
2020-03-12 Change filter and move stop_stepper wrapper outside of main
2020-03-12 Add EM3242 calibration--a rough first pass
2020-03-14 Add explicit gain term. Begin implementing linear servo control
2020-03-14 Add more computations for linear servo feedback
2020-03-15 Add FLIR camera model and Spinnaker version
2020-03-17 Reverse linear servo closed loop
2020-04-07 Add filter plotting and touch-up fft plotting
2020-04-08 Compute framerate by default
2020-04-08 Add framerate is None cond for filter
2020-04-08 Add commented out move for lin servo
2020-04-10 Fix avg framerate compute looping
2020-05-06 compute framerates from inst time
2020-05-06 compute mean framerate for filtering only
2020-06-20 show filtered speed cmap
2020-06-20 show filtered speed in cmap
2020-06-20 show filtered data
2020-06-22 use filtered data
2020-06-24 use filtered data for xy cmap
2020-06-24 rm redundant filtering
2020-06-29 add PID input to motor cmds
2020-06-29 print motor params before saving them
2020-06-29 move print_params for stepper below argparse args
2020-06-29 stop stepper when script is killed
2020-07-21 add stepper position as part of calib
2020-08-07 init PID filtering and normalization
2020-08-14 mkdir hardware and move subdirs into it
    [EM3242_breakoutboard_mount.dxf, clamping_mount_Uxcell_72_IR_LED_ring_to_InfiniGage.stl, connector_ball_fixture_to_3-8_tube.stl, floating_ball_fixture_10mm.fcst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]
2020-08-17 add working dual motor closed loops
2020-08-18 plot and save servo data
2020-08-18 put servo map outside of loop, change gain to 1
2020-08-21 scrap start_trigger fxn and use threading's Timer object
2020-08-21 start threading's Timer object
2020-08-21 join cam_timer thread
2020-08-25 add limits to servo extension and speed up back half retraction
2020-08-25 add local linear servo limits based on animal heading
2020-08-26 repeat stepper positioning as a hack to move back home counterclockwise
2020-09-26 rename dir
    [floating_ball_fixture_10mm.fcstd, floating_ball_fixture_10mm.step]
2020-09-26 add remaining hardware to make ring light mount
    [clamping_mount_for_waterjet.dxf, jig_for_milling_clamping_screw.stl]
2020-09-26 consolidate files for making mounting clamp
    [clamping_mount_for_waterjet.dxf, floating_ball_fixture_10mm.fcstd, floating_ball_fixture_10mm.step, jig_for_milling_clamping_screw.stl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]
2020-10-01 rm old nema17 adapter
    [nema17_42BYGHM810_to_14-20_breadboard_adaptor.dxf]
2020-10-01 accept only filtered df in compare_filtered_fictrac, do not filter in the fxn
2020-10-29 rename motor var col names
2020-11-24 move neck further out
    [slipring_immobilizer.stl]
2020-11-25 add DAQ counter, don't put cam trigger in own thread, clean other stuff
2020-11-26 fix imports and change while loop to cam timer thread, not omtor
2020-11-26 stop trigger at beginning in case still running before trig.start(); seems to work
2020-11-27 don't save elapsed times, just print them
2020-11-28 move to first stepper posn bf data acq
2020-11-29 fix stepper posn vels
2020-11-29 iniitialize daq and trigger bf socket connect
2020-11-30 plot absolute heading vs stepper posn, fix other stuff
2020-12-02 fix fictrac vs daq frame counting
2020-12-02 add another slipring immobilizer
    [slipring_opposite_immobilizer.stl]
2020-12-02 add piece to support two servo motors
    [support_layer1_doubled.dxf]
2020-12-04 fix doubled v of support layer 1
    [support_layer1_doubled.dxf]
2020-12-05 replace corrupted file
    [support_layer1_doubled.dxf]
2020-12-06 add layer 1 compatible with larger ball
    [support_layer1_doubled_platyusa_compatible.dxf]
2020-12-07 replace tap holes for brass inserts, and fix 1/4-20 hole sizes
    [clamping_mount_Uxcell_72_IR_LED_ring_to_InfiniGage.stl, clamping_mount_with_brass_inserts_Uxcell_72_IR_LED_ring_to_InfiniGage.stl]
2020-12-21 add ring light clamp to adapt infinigage to infinistix
    [clamping_mount_InfiniGage_to_InfiniStix_adaptor.stl]
2020-12-21 init switch box for IR lights
    [light_switch_box.stl, light_switch_lid.stl]
2020-12-22 init backlight on rail carrier
    [backlight_on_rail_carrier.stl]
2020-12-28 add D control to motor feedback
2021-01-12 change print time and add comment
2021-01-14 init pt_to_pt_expt but with streaming. elapsed times bw stream and motor does not align
2021-01-20 replace thread timer with atexit to stop trigger
2021-01-20 init module for getting motor commands
2021-01-20 add prints to atexit ritual
2021-01-20 rename print msg in home()
2021-01-20 rm threading import
2021-01-20 Rewrite. Subprocesses instead of threads. Use streams.
2021-01-20 add a global flag to kill stream_to_csv() if called in thread
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2021-01-21 add print msgs fix conditional on times
2021-01-22 fix stream motor to csv if duration is None
2021-01-23 does correct graceful exits and kills get motors thread ... had to use daemon w/ join, which is not ideal, oh well
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2021-02-16 fix bugs, tweak ordering, add more prints
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2021-10-29 fix all TODOs and add valve control support to pt_to_pt_expt
